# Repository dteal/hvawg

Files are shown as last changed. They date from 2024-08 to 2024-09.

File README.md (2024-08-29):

# High Voltage Arbitrary Waveform Generator

This is the first draft iteration of a modular arbitrary waveform generator intended to generate possibly tens of separate ±100V 1MHz signals for small capacitive loads, e.g., electrostatic actuators or ion traps.

WARNING: THIS BOARD IS DANGEROUS. IT USES SOMEWHAT HIGH VOLTAGES AT SOMEWHAT HIGH POWER. DO NOT BUILD, TEST, OR USE WITHOUT BOTH CAUTION AND KNOWING WHAT YOU ARE DOING. No guarantees or warranty or support is provided, etc.

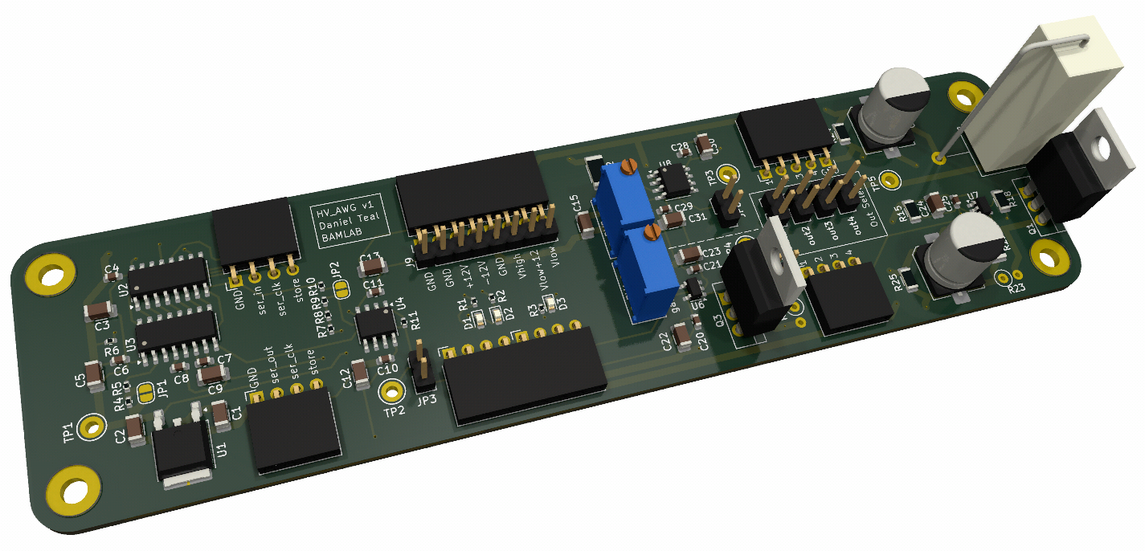
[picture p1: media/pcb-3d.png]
3D render of PCB


Specifications:
- serial data input at 3.3V or 5V up to maybe 100MHz, intended to be driven by FPGA
- 8-bit onboard DAC (with +/-1V output) (ENOB not measured but probably closer to 6 bits)
- amplifier with 100x gain gives outputs ±150V
- maximum output frequency is in the 100kHz range varying with load and voltage
- maximum designed load is tens of picofarads and megaohms of resistance
- up to four boards can be daisy-chained
- quiescent power consumption around 5 to 10W (b/c inefficient class A output stage)
- efficiency ≈1% (b/c inefficient class A output stage in open loop control)
- boards cost about $20 each and use only standard off-the-shelf parts

Measured frequency response:

(generated by feeding external signal into on-board amplifier bypassing DAC)

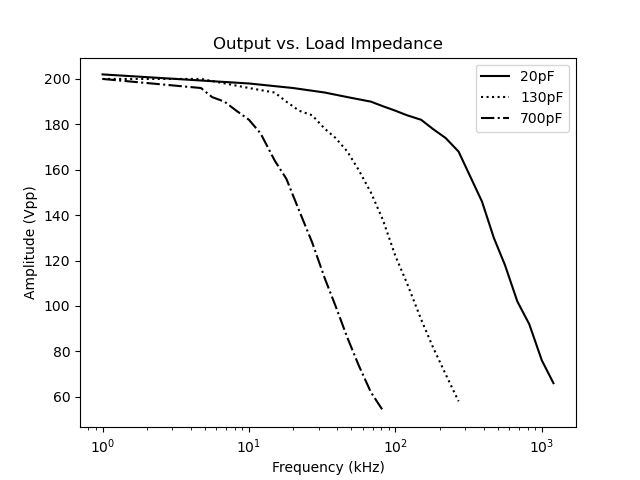
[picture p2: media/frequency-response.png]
frequency response curve


## Circuit Design

This circuit was made with the following constraints in mind:
- This is primarily intended to drive small capacitive loads, on the order of tens of picofarads with maybe megaohms of resistance. Note that oscilloscope input impedances are also about this much.
- Arbitrary waveform outputs between -100V and +100V and up to 1MHz. Either of those constraints is easy; together they are nontrivial. The ADHV4702 opamp can reach those voltages but only up to about 20kHz, for example.
- In order to have multiple outputs, multiple boards should be able to be daisy chained together. The final design allows up to four boards to be daisy chained and driven off a single 4-wire serial connection (three signals plus GND), for an average of 0.75 input signals per board, to drive as many boards as possible off of a single FPGA or other controller.
- Low cost. If tens of these boards are required for an application, each one should individually be cheap. This resulted in, e.g., five separate power supply inputs. The final part cost per board is around $20. Note a 2-layer PCB was used to decrease manufacturing time for external reasons; switching a 4-layer PCB or better is probably a good idea to allow better EMI mitigation techniques.
- DAC accuracy was not a priority. The original application needed less than 6 bits of resolution.
- Mass production. The circuit should not rely on manually matched transistors for a carefully-balanced amplifier. Instead, the output uses current mirrors that are cheaply implemented with off-the-shelf silicon power MOSFETs and don't require closed loop control on the output (which is not easily achieved at 1MHz at those voltages due to transistor switching time). (There is still manual tuning of amplifier gain and bias in order to minimize cost and accuracy, but this only has to be done once per board.)
- Robustness. The output can probably survive a short-circuit (untested).

The amplifier looks something like the following:

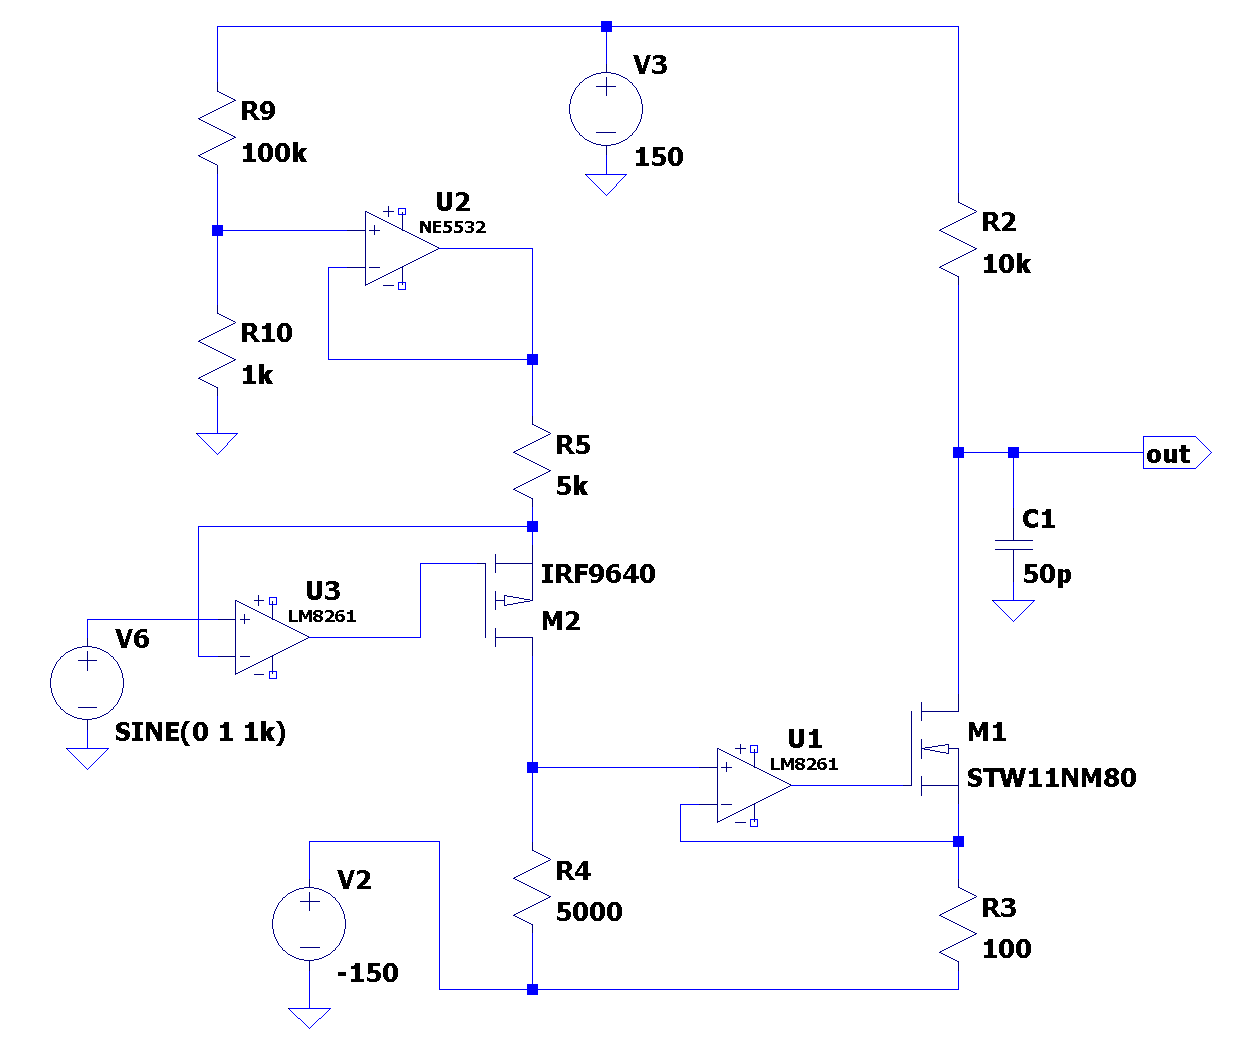
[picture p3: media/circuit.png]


### Alternatives

Previous but insufficient approaches to similar problems include:
- Using a high-voltage op-amp, e.g., the ADHV4702 <https://www.analog.com/en/products/adhv4702-1.html>. This can achieve the +/-100V range but only up to a bit over 20kHz.
- Resonant circuits. Common in ion traps and particle accelerators, but only generate a single specific frequency.
- Discrete amplifiers of assorted topologies, e.g., <https://doi.org/10.1063/1.1988272> or <https://doi.org/10.1063/1.3622750> or <https://www.radiolocman.com/shem/schematics.html?di=637101>. Note also <https://www.falco-systems.com/High_voltage_amplifier_WMA-300.html>. Commonly used for piezoelectric actuator drives, ultrasound, MEMS, or ion traps. These amplifiers achieve the required voltage and frequency specifications but are expensive and/or complex and rely on obscure components.

### Power input

This board takes five power inputs (in addition to the GND connection, of course):
- +12V (1W)
- -12V (1W)
- +100V (5W)
- -100V (5W)
- 12V above the -100V negative rail (1W)

These should be turned on in the following order:
1. +12V
2. -12V
3. +100V
4. -100V
5. 12V above -100V rail

LEDs indicate when the three 12V power supplies are on.

The power supplies used for testing were Wanptek WPS series supplies (160V 2A and 30V 10A) from eBay.

The +/-100V high voltage supplies are used to drive the output and need to be capable of the full board power draw (potentially 10W each, depending on component selection and voltage output).

The +/-12V supplies are used to drive the DAC and intermediate amplifier opamps. These are not generated from the +/-100V because a linear regulator would be too lossy and a buck regulator would make the board significantly more complex and expensive.
Likewise, the low 12V supply is used to drive the output amplifier opamp, and is not generated from the other supplies for the same efficiency reason.

If more convenience is required, an external board can generate the 12V and 100V supplies however desired.

### DAC

The DAC circuit takes a serial input via the 74HC595 shift register and sends the output to a DAC0909 DAC chip.

The DAC is 8 bits. Four PCBs can be daisy-chained together (requiring 32 bits).

The DAC should theoretically operate up to about 100MHz, allowing four 8-bit daisy-chained boards to be updated at above 1MHz. This upper speed has not been tested yet and may be limited by inferior PCB routing.

The DAC protocol works (via the 74HC595) as follows:
- Input signals at 3.3V or 5V should both work.
- 4 pins are required (GND, store_clock, shift_clock, and serial_in).
- First, data is sent in via serial_in at each rising edge of the shift_clock.
- Next, when store_clock is brought high, the current state of the data is saved and sent to the DAC.

This should work with any 74HC595 code, e.g., many Arduino libraries.

### Level shifter

The level shifter circuit accepts an input +/-1V analog signal, translates this into a current, and sends the result to the negative high voltage rail, where it is converted back into an analog voltage to drive the output opamp.

The level shifter can be disconnected from the DAC via jumper JP3 in order to input an external analog signal (e.g., from a low-voltage waveform generator) for testing purposes.

Potentiometer RV1 controls the gain of the high voltage output and should be adjusted to give a 100x amplification.

NOTE: THE CURRENT PCB HAS AN ERROR (see "Errata" below) where the source and drain of PMOS transistor Q3 are switched. If this is not fixed during assembly, when the high voltage low rail is turned on, significant current will flow through R17, which will burn out due to excessive power draw.

### High side monitor circuit

This subcircuit provides compensation such that the final high-voltage output is independent of the high voltage supply level (i.e., high voltage inputs of +50V, +100V, and +150V should not affect a 50Vpp output signal).

Potentiometer RV2 controls the DC bias of the output and should be adjusted to center the output at GND = 0V.

Resistor R12=110kohm dissipating up to 200mW was specifically chosen to minimize power draw while also maximizing the voltage/current at the input to opamp U8A (which has nonzero input offset current).

### Output amplifier

This circuit takes an input voltage signal near the negative rail (from the level shifter) and converts this into a current signal through Q1 and R21, which form a class-A amplifier to generate the final high-voltage output. The output voltage is determined by the voltage drop of R21 with the given current.

R21 and Q1, as a class-A amplifier, form a resistive divider between the high voltage power rails, and dissipate a large (10W) current even in their quiescent state in order to drive loads with reasonable accuracy. This means they generate significant heat.

R21 was chosen at 10k as a reasonable compromise between quiescent power draw and load drive ability. R21 can be replaced with a 5kohm power resistor to draw more current but double the output load capacity.

### Output

The final output from R21 and Q1 can be connected to any one of outputs 1 through 4 via jumpers JP8 through JP11.

Four daisy-chained boards can thus be attached to separate outputs.

## Assembly and Testing

### Part choice notes

- All SMD parts are from JLCPCB and specifically chosen from parts with reliable high stock.

- Hand-soldered components were added manually afterward (not through JLCPCB) to reduce order lead time.

### Manufacturing notes

These boards were designed in KiCad and ordered from JLCPCB with help from the excellent kicad-jlc-pcb tools plugin <https://github.com/bouni/kicad-jlcpcb-tools>.

### Assembly notes

Hand assembly of the through hole components takes about 20 minutes per board.

Be sure to bend the legs of the PMOS MOSFET to switch its source and drain to fix a board error (see "Errata" section below).

Header pins are ordered in lenths of 18 to reduce costs. These should be manually cut to size (or ordered in the right size to begin with).

The power resistor R21 needs spare wires soldered on to fit the PCB footprint. The resistor hangs off the edge of the board so it can be bolted to a heatsink. It's possible these spare wires increase EMI emissions. Future board iterations could switch to a TO-220 package power resistor, matching NMOS transistor Q1, which is also at the edge of the board for easy heatsink mounting.

### Bringup notes

After the board is assembled, the following bringup/test strategy seems to work well:

- Start with jumpers JP3, JP4, and JP6 disconnected. Connect one of JP8, JP9, JP10, JP11 to choose output.
- Test DAC. Apply +12V then -12V supply (if +12V but not -12V is applied too long, DAC may heat up). Confirm LEDs light up. Add DAC input signal. Use thermal camera to confirm no major hot spots (NE5532 opamps at 35°C, LEDs at 32°C, not much else).
- Confirm DAC output is good (TP2/JP3 via oscilloscope). Full scale output is around 2.8Vpp.
- Test high voltage monitor circuit. Attach +120V supply, confirm high voltage monitor output (TP3 via multimeter) is stable and good and in the 1 to 3V range. R12 should rise in temperature (maybe 36°C) due to its 200mW power dissipation.
- Turn off power supplies and add jumpers JP3, JP6.
- Test level shifter. Apply +12V, -12V, +120V, and -120V. Confirm temperatures good (no significant change from before).
- Confirm DAC and monitor outputs remain good.
- Confirm level shifter output is sine wave (measure JP4 oscilloscope with AC coupling).
- Turn supplies off again, add jumper JP4.
- Test final output stage. Turn supplies on, including +12V on negative rail this time (additional LED should come on).
- Confirm only thermal change is output resistor and MOSFET heating to maybe 60-80°C (if supplies are +/-120V).
- Confirm final board output (measured at TP5, output port, or resistor lead via DC-coupled multimeter) is expected signal. Might be DC shifted and cut off at high/low rail.
- Adjust RV2 to center output wave at 0V.
- Adjust RV1 to set gain to get about +/-100V output. Can set to +/-128V full-scale output so that a 1 bit input change results in 1V output change.

### SMD components (JLCPCB)

| Part no.          | QTY | Cost | JLC type | Note                      | URL                                                                    |
|-------------------|-----|------|----------|---------------------------|------------------------------------------------------------------------|
| 74HC595D,118      |   1 | 0.10 | basic    | shift register            | https://jlcpcb.com/partdetail/Nexperia-74HC595D118/C5947               |
| DAC0808LCMX/NOPB  |   1 | 1.80 | extended | dac                       | https://jlcpcb.com/partdetail/TexasInstruments-DAC0808LCMXNOPB/C132006 |
| NE5532DR          |   2 | 0.15 | basic    | opamp                     | https://jlcpcb.com/partdetail/TexasInstruments-NE5532DR/C7426          |
| LM8261M5X/NOPB    |   2 | 2.12 | extended | opamp                     | https://jlcpcb.com/partdetail/TexasInstruments-LM8261M5XNOPB/C7968     |
| L78M05ABDT-TR     |   1 | 0.13 | basic    | 5V regulator              | https://jlcpcb.com/partdetail/Stmicroelectronics-L78M05ABDTTR/C58069   |
| KT-0603W          |   3 | 0.01 | basic    | white 0603 LED            | https://jlcpcb.com/partdetail/Hubei_KentoElec-KT0603W/C2290            |
| RT0402BRE072K74L  |  12 | 0.02 | extended | 2.74kohm 0402 0.1% 62.5mW | https://jlcpcb.com/partdetail/Yageo-RT0402BRE072K74L/C705647           |
| WR20X750JTL       |   1 | 0.02 | extended | 75ohm 2010 200V           | https://jlcpcb.com/partdetail/Walsin_TechCorp-WR20X750JTL/C172257      |
| 1206W4F1004T5E    |   4 | 0.01 | basic    | 1Mohm 1206 200V 250mW     | https://jlcpcb.com/partdetail/18615-1206W4F1004T5E/C17927              |
| UD2D4R7M0810      |   2 | 0.08 | extended | 4.7uF 200V SMD            | https://jlcpcb.com/partdetail/HonorElec-UD2D4R7M0810/C88701            |
| CC0603KRX7R9BB104 |  12 | 0.01 | basic    | 100nF 0603 50V            | https://jlcpcb.com/partdetail/Yageo-CC0603KRX7R9BB104/C14663           |
| CL31A106KBHNNNE   |  13 | 0.03 | basic    | 10uF 1206 50V             | https://jlcpcb.com/partdetail/14236-CL31A106KBHNNNE/C13585             |
| 2010W2J0114T4S    |   1 | 0.01 | extended | 110kohm 2010 200V 500mW   | https://jlcpcb.com/partdetail/21062-2010W2J0114T4S/C20351              |

### Through-hole components (manually added afterward)

| Part no.       | QTY | Cost  | Note                  | URL                                                                                           |
|----------------|-----|-------|-----------------------|-----------------------------------------------------------------------------------------------|
| 3296Y-1-472LF  |   2 | $1.3  | 4.7kohm trimpot       | https://www.digikey.com/en/products/detail/bourns-inc/3296Y-1-472LF/2536016                   |
| IRF9610PBF     |   1 | $1.1  | PMOS power FET        | https://www.digikey.com/en/products/detail/vishay-siliconix/IRF9610PBF/811768                 |
| IRF730PBF      |   1 | $1.1  | NMOS power FET        | https://www.digikey.com/en/products/detail/vishay-siliconix/IRF730PBF/811793                  |
| QPC02SXGN-RC   |   4 | $0.04 | jumper                | https://www.digikey.com/en/products/detail/sullins-connector-solutions/QPC02SXGN-RC/2618262   |
| THS2510KJ      |   1 | $2.5  | 10kohm power resistor | https://www.digikey.com/en/products/detail/te-connectivity-passive-product/THS2510KJ/2366983  |
| PREC018SABN-RC |   3 | $0.25 | 18-pin male header    | https://www.digikey.com/en/products/detail/sullins-connector-solutions/PREC018SABN-RC/2775036 |
| PPPC181LGBN-RC |   3 | $0.82 | 18-pin female header  | https://www.digikey.com/en/products/detail/sullins-connector-solutions/PPPC181LGBN-RC/775951  |

## Errata and Future Improvements

Board error:
- The PMOS transistor (Q3) source and drain pins are switched on the PCB. This can be fixed when hand-soldering by bending the MOSFET legs to fit the right holes. Not doing this causes excessive current through R17, burning it out, with possible additional damage to RV1.

EMI issue:
- I suspect this board might sometimes generate nontrivial RF noise. Qualitative tests show unshielded wires on the output (or maybe even the wires connecting the through-hole power resistor) generate an undesired signal. Thus, be very careful with board use. Future board iterations should fix this issue by, e.g., more careful PCB trace design and changing the signal output connector to a shielded RF SMA connector or similar.

Improvements:
- The first iteration used a 25W chassis-mount power resistor, which worked fine without heatsinking but needed manual wiring to the PCB. To avoid the inconvenience of having a component not directly mounted to the PCB, future iterations might consider using a TO-220 package power resistor and heatsinking instead (e.g., AP836 10K J, https://www.digikey.com/en/products/detail/ohmite/AP836-10K-J/5878547 ).
- A 2-layer PCB was used to decrease manufacturing time for external reasons; switching a 4-layer PCB or better is probably a good idea to allow better EMI mitigation techniques.

## Images

### 3D render

3D render of PCB

### Assembled PCBs

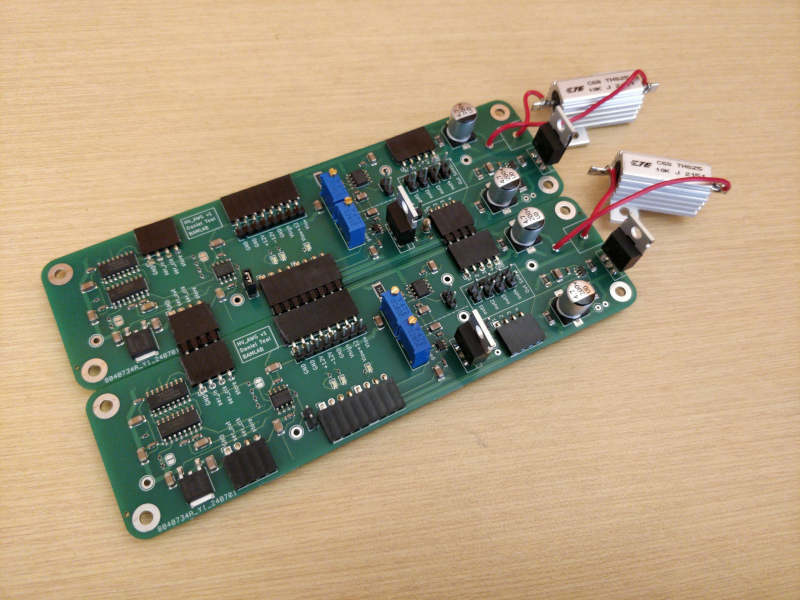
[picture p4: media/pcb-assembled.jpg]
Two assembled PCBs


### Thermal testing

Note the hottest parts of the circuit are the power resistor and MOSFET near the output, as expected.

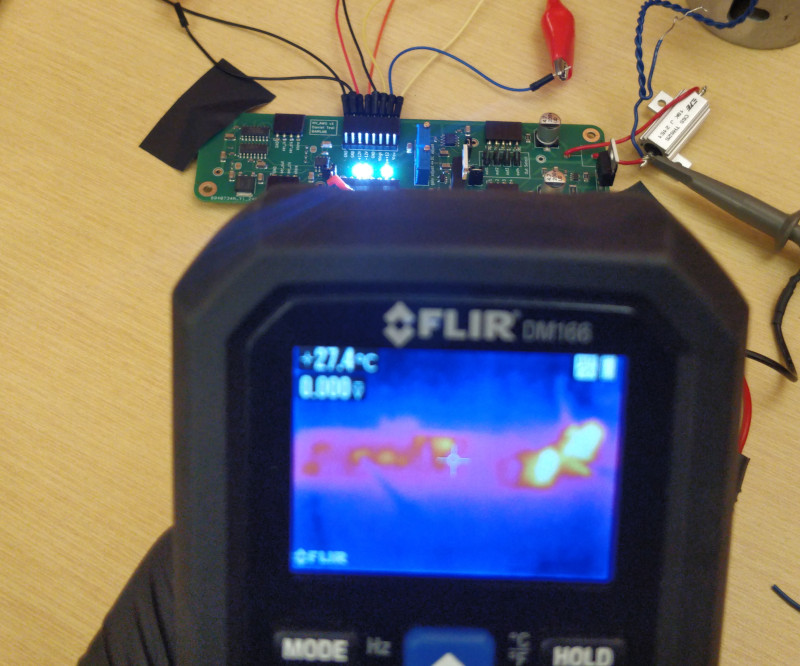
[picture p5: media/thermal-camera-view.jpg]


### Frequency response testing

An external function generator was used to generate test waveforms by disconnecting the DAC via jumper JP3.

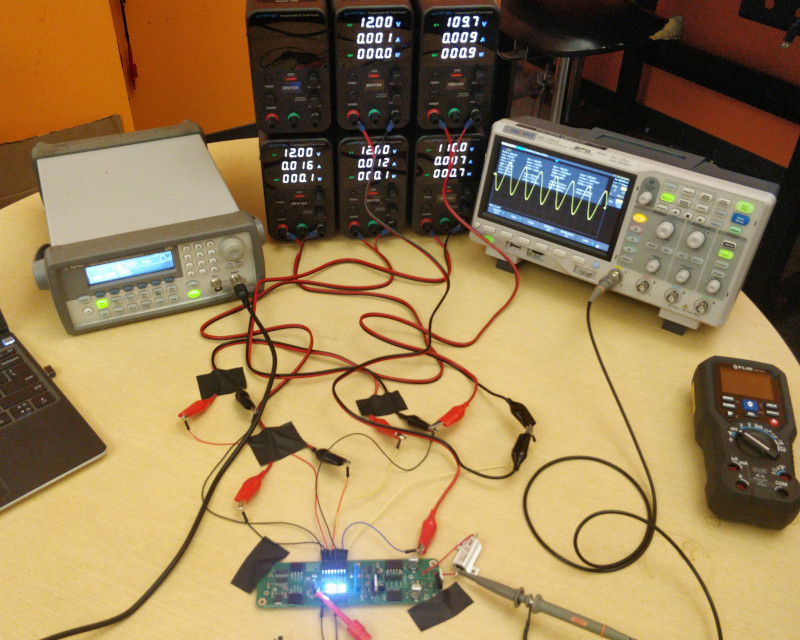
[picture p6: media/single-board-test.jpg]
frequency response test setup


### Daisychain test

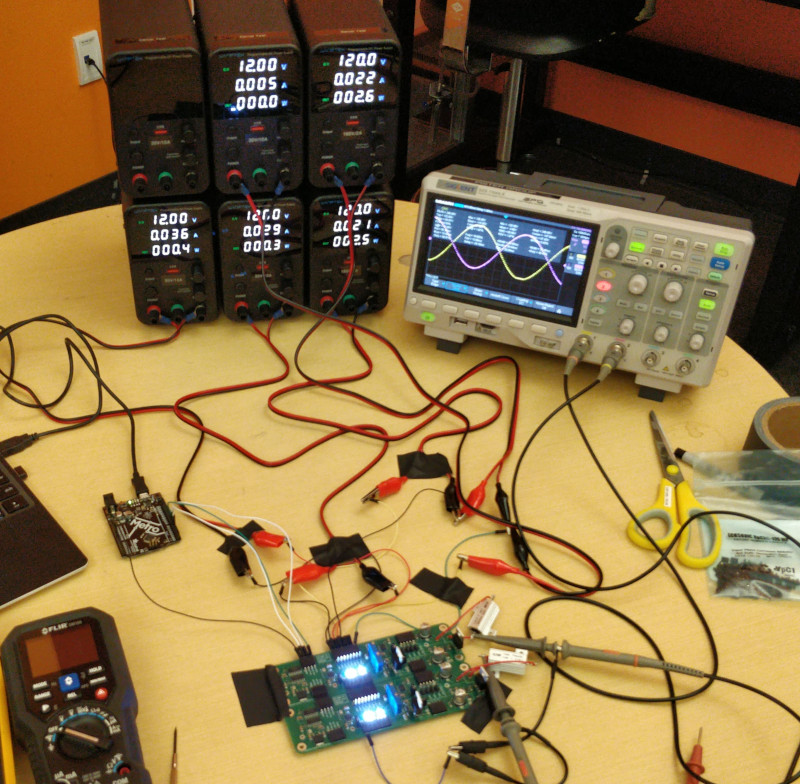
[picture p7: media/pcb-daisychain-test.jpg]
Two boards generating 200Vpp 1kHz waves


### PCB frame concept

Heatsinks, external wires, and control board not included. Note a large flat heatsink is easy to add along the output power resistors and MOSFETs.

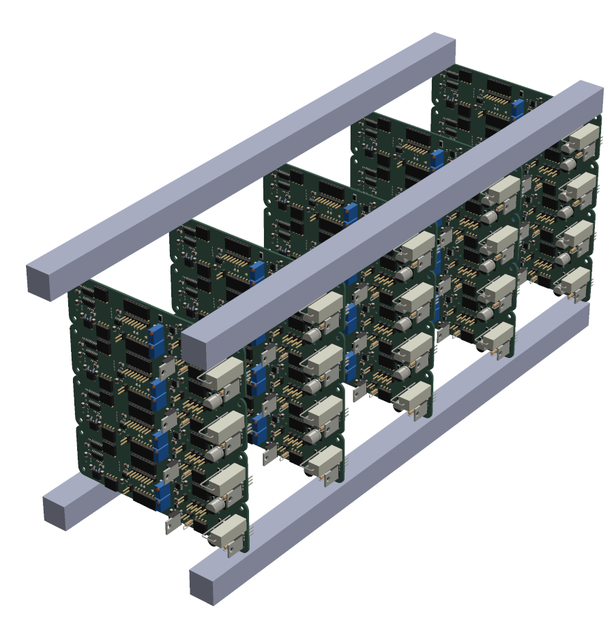
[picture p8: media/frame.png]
PCB frame concept


### EMI Issue

Several-foot-long unshielded wires connected to the output and a capacitive load interfere with the signal generator. Note the waveform on the oscilloscope only shows half a sinusoid; the lower half was somehow blocked. The test was immediately stopped.

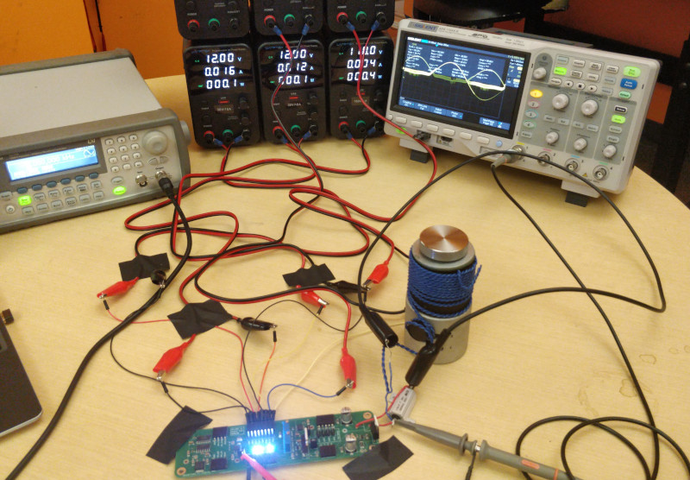
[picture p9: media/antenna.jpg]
EMI discovery


Using a shielded cable reduced interference, but that's still not a perfect sinusoid on the oscilloscope. Recommendation: improve PCB to minimize external wires and other possible EMI sources and use a proper RF SMA connector for the output.

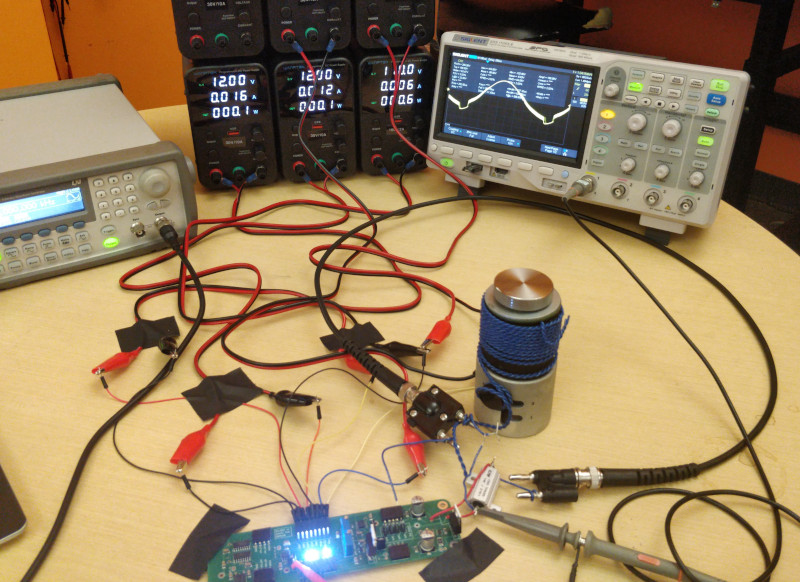
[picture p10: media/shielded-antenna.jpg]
lower EMI with shielded cable


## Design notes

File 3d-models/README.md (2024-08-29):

# 3D Models

`hvawg.step` is a 3D model of the assembled board with components exported by KiCad.

Other files are partially complete models from SolidWorks in assorted stages of completion.

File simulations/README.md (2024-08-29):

# Simulations

All simulations made with LTSpice.

`class-a-amplifier-test.asc`: Simulation of class A output stage. Works well. Good for rapid idea testing.

`full-amplifier-test.asc`: Simulation of full amplifier circuit. Works slowly. Has trouble converging.

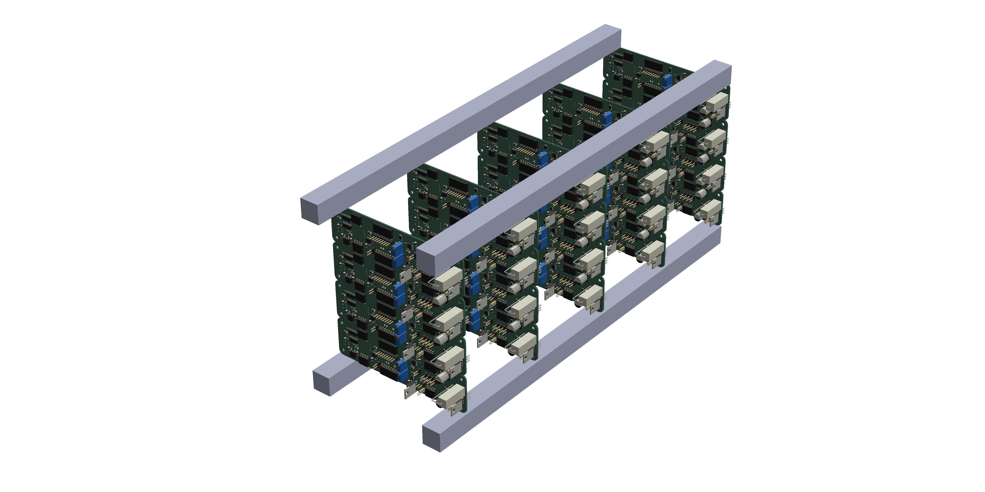
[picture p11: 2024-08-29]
3d-models/frame.PNG

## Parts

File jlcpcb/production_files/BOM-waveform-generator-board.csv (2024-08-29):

Comment | Designator | Footprint | LCSC
DAC0808LCMX/NOPB | U3 | SOIC-16_3.9x9.9mm_P1.27mm | C132006
10u | C1,C12,C13,C15,C2,C22,C23,C24,C3,C30,C31,C5,C9 | C_1206_3216Metric | C13585
100n | C10,C11,C14,C20,C21,C25,C28,C29,C4,C6,C7,C8 | C_0603_1608Metric | C14663
75 | R22 | R_2010_5025Metric | C172257
1M | R15,R18,R24,R25 | R_1206_3216Metric | C17927
110k | R12 | R_2010_5025Metric | C20351
LED | D1,D2,D3 | LED_0603_1608Metric | C2290
L7805 | U1 | TO-252-2 | C58069
74HC595D,110 | U2 | SOIC-16_3.9x9.9mm_P1.27mm | C5947
2.7k | R1,R10,R11,R17,R2,R3,R4,R5,R6,R7,R8,R9 | R_0402_1005Metric | C705647
NE5532 | U4,U8 | SOIC-8_3.9x4.9mm_P1.27mm | C7426
LM8261 | U6,U7 | SOT-23-5 | C7968
4.7u | C26,C27 | CP_Elec_8x10.5 | C88701

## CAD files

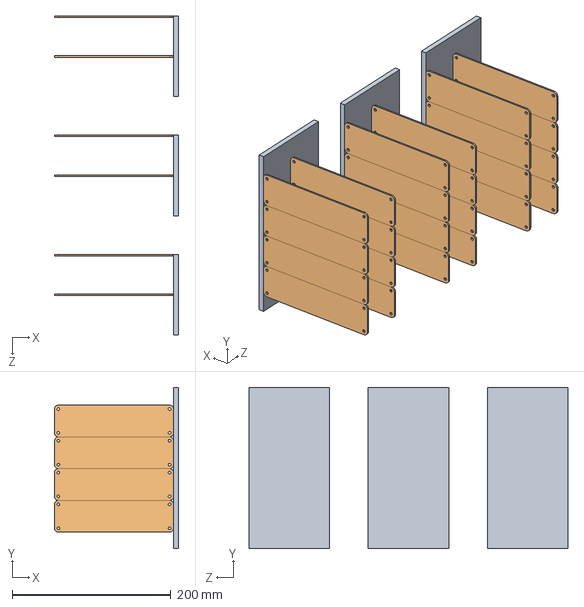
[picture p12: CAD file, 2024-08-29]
3d-models/waveform-pcb-assembly.SLDASM
156.3 x 203.2 x 401.6 mm
PCB x 24
heatspreader x 3

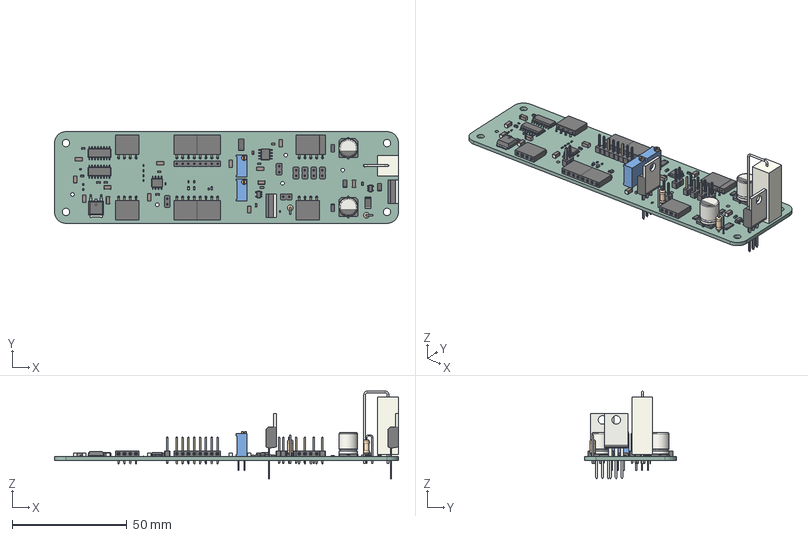
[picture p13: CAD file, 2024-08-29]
3d-models/hvawg.step
150.0 x 40.0 x 38.3 mm
SOIC_16_39x99mm_P127mm x 2
C_1206_3216Metric x 13
R_Axial_Power_L250mm_W90mm_P1016mm_Vertical
SOT_23_5 x 2
R_2010_5025Metric x 2
R_0402_1005Metric x 12
LED_0603_1608Metric x 3
PinSocket_1x04_P254mm_Horizontal x 8
Potentiometer_Bourns_3296Y_Vertical x 2
C_0603_1608Metric x 12
CQ assembly
PinHeader_1x08_P254mm_Vertical
R_Axial_DIN0207_L63mm_D25mm_P254mm_Vertical x 2
PinHeader_1x02_P254mm_Vertical x 7
R_1206_3216Metric x 4
TO-220-3_Vertical x 2
SOIC_8_39x49mm_P127mm x 2
CP_Elec_8x105 x 2
PinSocket_1x01_P254mm_Horizontal
hvawg_PCB

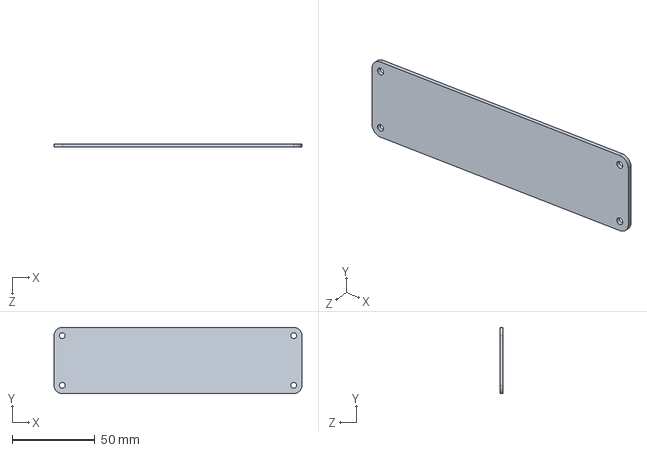
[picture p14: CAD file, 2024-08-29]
3d-models/PCB.SLDPRT
150.0 x 40.0 x 2.00 mm

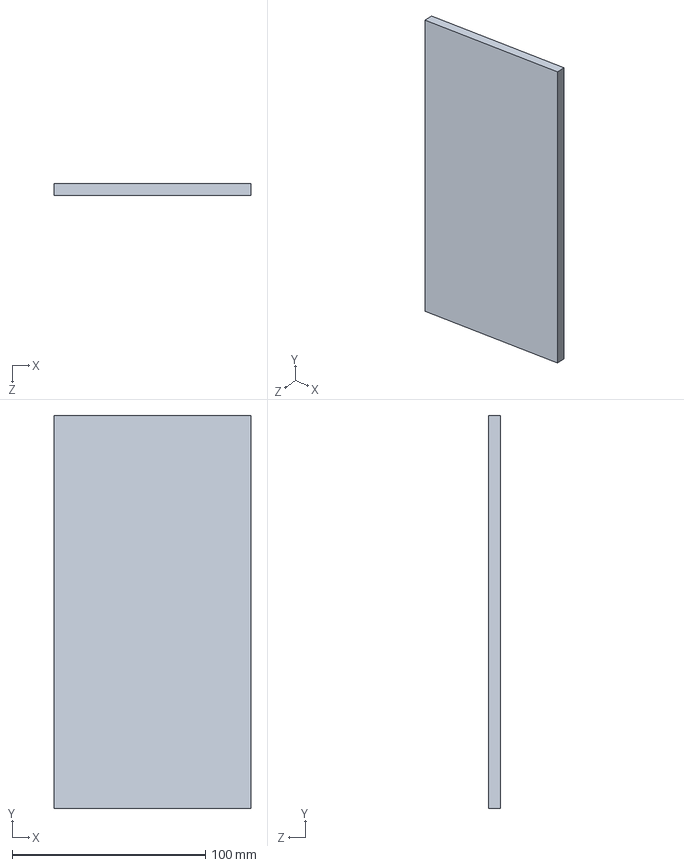
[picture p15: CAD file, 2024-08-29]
3d-models/heatspreader.SLDPRT
101.6 x 203.2 x 6.35 mm

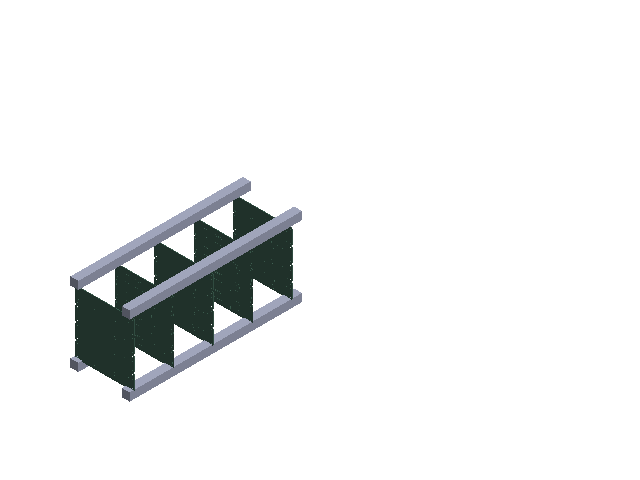
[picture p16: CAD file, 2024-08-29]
3d-models/complete-assembly.SLDASM
waveform-generator-board_PCB.step x 20
frame

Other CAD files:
3d-models/waveform-generator-board.SLDASM
3d-models/frame.SLDPRT

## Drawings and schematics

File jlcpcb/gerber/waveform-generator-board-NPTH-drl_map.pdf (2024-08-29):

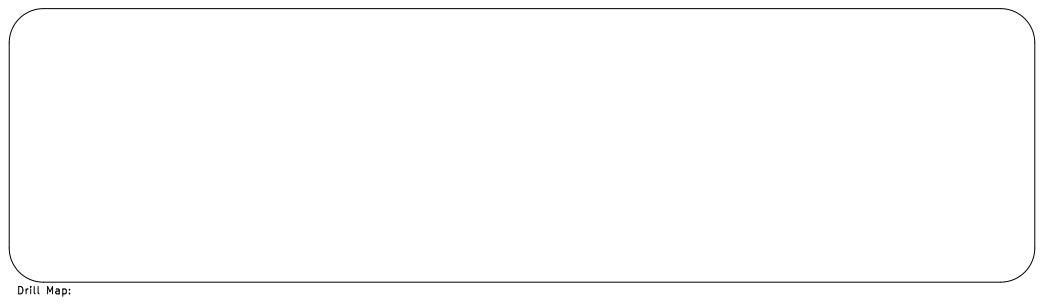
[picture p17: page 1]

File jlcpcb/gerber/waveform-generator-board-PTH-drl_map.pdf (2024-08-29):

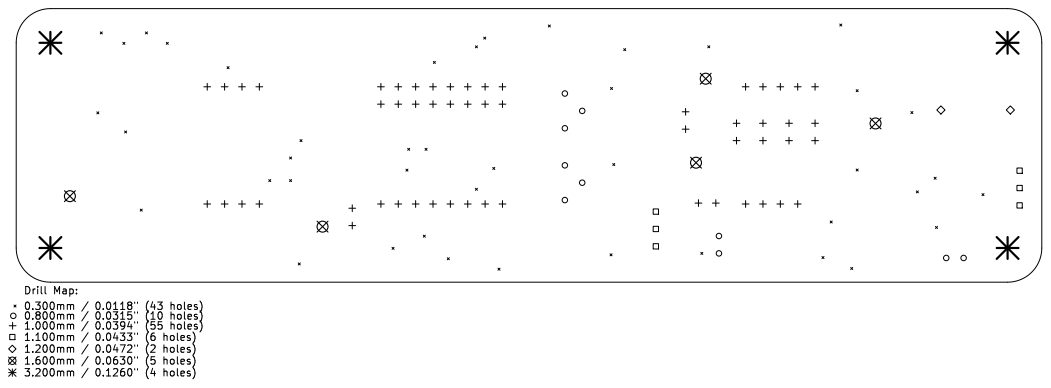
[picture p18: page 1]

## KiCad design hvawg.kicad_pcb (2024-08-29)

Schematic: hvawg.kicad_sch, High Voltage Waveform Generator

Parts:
C1, C2, C3, C5, C9, C12, C13, C15, C22, C23, C24, C30, C31: 10u; C_1206_3216Metric
C4, C6, C7, C8, C10, C11, C14, C20, C21, C25, C28, C29: 100n; C_0603_1608Metric
C26, C27: 4.7u; CP_Elec_8x10.5
D1, D2, D3: LED; LED_0603_1608Metric
H1, H2, H3, H4: MountingHole; MountingHole_3.2mm_M3_Pad
J1, J3, J5, J7: Conn_01x04_Pin; PinSocket_1x04_P2.54mm_Horizontal_flipped
J2, J4, J6, J8: Conn_01x04_Pin; PinSocket_1x04_P2.54mm_Horizontal
J9: Conn_01x08_Pin; PinHeader_1x08_P2.54mm_Vertical
J10: Conn_01x01_Pin; PinSocket_1x01_P2.54mm_Horizontal
JP1: SolderJumper_2_Open; SolderJumper-2_P1.3mm_Open_RoundedPad1.0x1.5mm
JP2: SolderJumper_2_Bridged; SolderJumper-2_P1.3mm_Bridged_RoundedPad1.0x1.5mm
JP3, JP4, JP6: Jumper_2_Bridged; PinHeader_1x02_P2.54mm_Vertical
JP8, JP9, JP10, JP11: Jumper_2_Open; PinHeader_1x02_P2.54mm_Vertical
Q1: IRF730; TO-220-3_Vertical
Q3: IRF9610; TO-220-3_Vertical
R1, R2, R3, R4, R5, R6, R7, R8, R9, R10, R11, R17: 2.7k; R_0402_1005Metric
R12: 110k; R_2010_5025Metric
R15, R18, R24, R25: 1M; R_1206_3216Metric
R19, R23: 100; R_Axial_DIN0207_L6.3mm_D2.5mm_P2.54mm_Vertical; not fitted
R21: 10k; R_Axial_Power_L25.0mm_W9.0mm_P10.16mm_Vertical
R22: 75; R_2010_5025Metric
RV1: 3k; Potentiometer_Bourns_3296Y_Vertical
RV2: 1k; Potentiometer_Bourns_3296Y_Vertical
TP1, TP2, TP3, TP4, TP5: TestPoint; TestPoint_Keystone_5005-5009_Compact
U1: L7805; TO-252-2
U2: 74HC595D,110; SOIC-16_3.9x9.9mm_P1.27mm
U3: DAC0808LCMX/NOPB; SOIC-16_3.9x9.9mm_P1.27mm
U4, U8: NE5532; SOIC-8_3.9x4.9mm_P1.27mm
U6, U7: LM8261; SOT-23-5

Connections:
+12V: C1.1, C10.1, C12.1, C20.1, C22.1, C28.1, C30.1, J3.3, J4.3, J9.3, R1.1, U1.1 (IN), U4.8 (V+), U6.5 (V+), U8.8 (V+)
+100V: C26.1, J5.2, J6.2, J9.6, R12.1, R21.2, R24.1
-12V: C7.1, C8.2, C9.1, C11.1, C13.1, C21.1, C23.1, C29.1, C31.1, J3.4, J4.4, J9.4, R2.2, U3.7 (VEE), U4.4 (V-), U6.2 (V-), U8.4 (V-)
-100+12V: C24.2, C25.2, J5.3, J6.3, J9.7, R3.1, R15.2, U7.5 (V+)
-100V: C24.1, C25.1, C27.2, D3.1 (K), J5.4, J6.4, J9.8, R15.1, R17.2, R18.2, R19.2, R22.2, R23.1, R25.2, U7.2 (V-)
GND: C1.2, C2.2, C3.2, C4.2, C5.2, C6.2, C7.2, C9.2, C10.2, C11.2, C12.2, C13.2, C14.2, C15.2, C20.2, C21.2, C22.2, C23.2, C26.2, C27.1, C28.2, C29.2, C30.2, C31.2, D1.1 (K), D2.2 (A), J1.1, J2.1, J3.1, J3.2, J4.1, J4.2, J5.1, J6.1, J9.1, J9.2, J9.5, J10.1, R6.2, R10.2, R24.2, R25.1, RV2.2, U1.2 (GND), U2.8 (GND), U2.13 (~OE), U3.6 (GND)
unnamed: D1.2 (A), R1.2
unnamed: D2.1 (K), R2.1
unnamed: D3.2 (A), R3.2
unnamed: J7.1, J8.1, JP8.2 (B)
unnamed: J7.2, J8.2, JP9.2 (B)
unnamed: J7.3, J8.3, JP10.2 (B)
unnamed: J7.4, J8.4, JP11.2 (B)
unnamed: JP1.1 (A), R4.2, R5.1
unnamed: C2.1, C3.1, C4.1, C5.1, C6.1, JP1.2 (B), R4.1, R7.1, TP1.1, U1.3 (OUT), U2.10 (~SRCLR), U2.16 (VCC), U3.1 (VCC)
unnamed: JP2.1 (A), R10.1
unnamed: JP2.2 (B), R9.2, U4.3 (+)
unnamed: JP3.2 (B), U6.3 (+)
unnamed: JP4.2 (B), U7.3 (+)
unnamed: JP6.1 (A), RV1.1
unnamed: JP8.1 (A), JP9.1 (A), JP10.1 (A), JP11.1 (A), Q1.2 (D), R21.1, TP5.1
unnamed: Q1.1 (G), R18.1, U7.1
unnamed: Q1.3 (S), R22.1, R23.2, U7.4 (-)
unnamed: Q3.2 (D), RV1.2, U6.4 (-)
unnamed: Q3.1 (G), U6.1
unnamed: R7.2, R8.1
unnamed: R8.2, R9.1
unnamed: U2.15 (QA), U3.16 (A8)
unnamed: U2.1 (QB), U3.15 (A7)
unnamed: U2.2 (QC), U3.14 (A6)
unnamed: U2.3 (QD), U3.13 (A5)
unnamed: U2.4 (QE), U3.12 (A4)
unnamed: U2.5 (QF), U3.11 (A3)
unnamed: U2.6 (QG), U3.10 (A2)
unnamed: U2.7 (QH), U3.9 (A1)
unnamed: C8.1, U3.4 (COMPEN)
unnamed: R5.2, U3.2 (VREF+)
unnamed: R6.1, U3.3 (VREF-)
unnamed: R11.1, U4.1, U4.2 (-)
unnamed: C14.1, C15.1, R12.2, RV2.1, U8.3 (+)
dac_out: JP3.1 (A), R11.2, TP2.1, U3.8 (I0)
levelshift_out: JP4.1 (A), Q3.3 (S), R17.1, R19.1, TP4.1
monitor_out: JP6.2 (B), TP3.1, U8.1, U8.2 (-)
serial_in: J1.2, U2.14 (SER)
serial_out: J2.2, U2.9 (QH')
shift_clock: J1.3, J2.3, U2.11 (SRCLK)
store_clock: J1.4, J2.4, U2.12 (RCLK)

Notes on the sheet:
Vds_max > 300V rise/fall < 500ns 10W or greater small gate cap
Level shifter
LM8261M5X/NOPB > 20MHz GBWP high cap drive supply range > 10V
100x divider Choose divider to minimize power but also have greater current than NE5532 bias current (~500nA)
provided via external supply; opamp draws up to 0.1W so linear regulation from >100V is inefficient
average 0.1k (for 5k) or 2.8k (for 10k out) adjust 0-4.7k
1k average adjust 0 to 4.7k (coarse adjust)
use generic 0603 SMD LEDs assume 5-10mA current draw use 1k-3k resistors
L78M05ABDT-TR
Use this to determine amplifier gain Mirror gives ~50x This should be ~2x So adjust resistor to about half of Rout, i.e., 2.5 to 5kohm. Also needs sufficient precision to get <0.5% (1 LSB)
Power
thru-hole, just in case
note NE552DR has low slew rate can handle maybe 2.5Vpp max at 1MHz
in case I need a gate resistor
1:4 voltage divider (1.25V output)
5V regulator - makes 74HC595 both fast and able to receive 3.3V inputs - only needs ~10% accuracy as long as it is stable/precise (amplifier gain can be used to compensate) - probably want 1W part?
> 200V
for cable ground shield
larger than MOSFET gate
power resistor 10W or greater
set gate=0V if opamp off
bleed resistors > 200V
DAC
Dissipates ~200mW so use 1W package!
High side monitor
choose value so mirror amplification is a bit less than 50x. also use max current possible w/o excessive power dissipation, to reduce errors from opamp bias current 10k Rout -> max 600uA, average 300uA 5k Rout -> max 1200uA, average 600uA LM8261 bias current is ~1uA (and there are two), so set 1 LS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
output constant 1.25V
Mechanical
matched resistors
10k Rout -> max 30mA, average 15mA 5k Rout -> max 60mA, average 30mA set control voltage ~=1V to keep R_mirror_out < 100mW
tie to negative rail if supply disconnects
Amplifier
need 2.5k to 5k ohm total (for 5k or 10k Rout) (with 55:1 ratio: need 2.7k-5.5kohm)

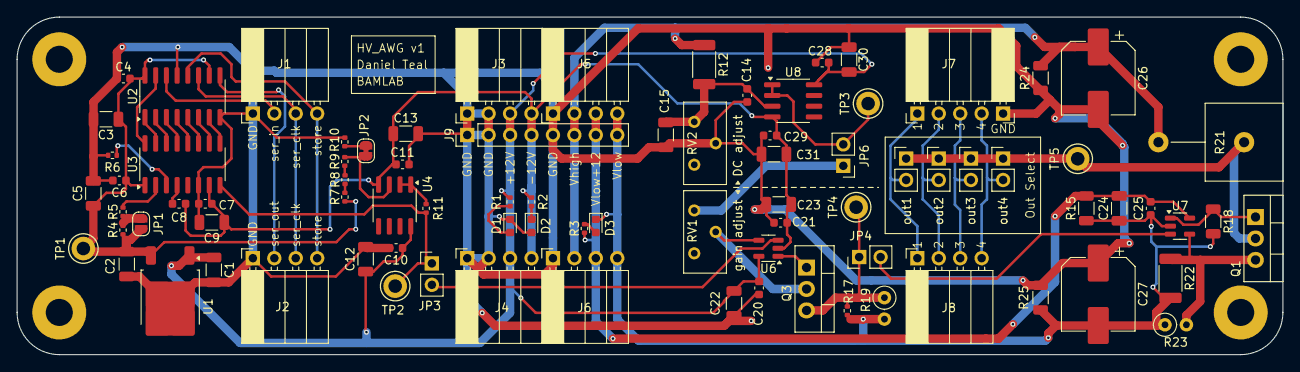
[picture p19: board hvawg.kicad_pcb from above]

Board: 2 copper layers, 150.0 x 40.0 mm, 90 parts (0 on the bottom side), 47 nets.

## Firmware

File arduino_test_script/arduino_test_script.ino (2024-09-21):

int latchPin = 5; // 74HC595 ST_CP
int clockPin = 6; // 74HC595 SH_CP
int dataPin = 4;  // 74HC595 DS

byte data = 0;
float freq = 1000.0f; // 1khz

void setup(){
  data = 0;
  pinMode(latchPin, OUTPUT);
  pinMode(dataPin, OUTPUT);
  pinMode(clockPin, OUTPUT);
}

void loop(){
  data = int(128+128*sin(2*3.14159*micros()/50000.0f));
  digitalWrite(latchPin, LOW);
  shiftOut(dataPin, clockPin, MSBFIRST, data);
  digitalWrite(latchPin, HIGH);
  delayMicroseconds(1);
}

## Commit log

2024-08-29 Initial upload
    [hvawg.kicad_pcb, hvawg.kicad_sch]
2024-08-29 Add initial JLCPCB files
    [BOM-waveform-generator-board.csv, CPL-waveform-generator-board.csv, waveform-generator-board-CuBottom.gbr, waveform-generator-board-CuTop.gbr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]
2024-08-29 Added circuit to README
2024-08-29 Add PCB layer info
2024-08-29 Add assembly details
2024-08-29 Add power supply source note
2024-08-29 Add 3D models
    [PCB.SLDPRT, complete-assembly.SLDASM, frame.SLDPRT, heatspreader.SLDPRT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]
2024-09-21 Added simple Arduino test script. Generates waves up to ~20Hz.
